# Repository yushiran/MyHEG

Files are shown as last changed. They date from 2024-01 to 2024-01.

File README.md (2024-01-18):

# 设计一下MyHEG(max30102)的detector pcb
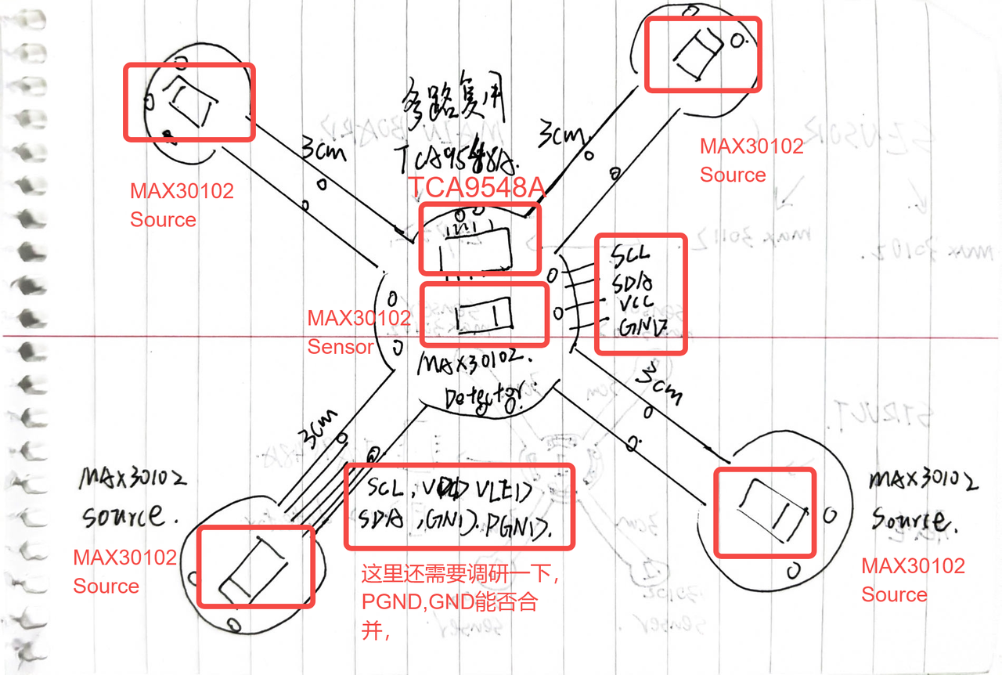
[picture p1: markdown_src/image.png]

## 设计思路：
要参考一下这篇review：https://joi.usst.edu.cn/html/2022/5/20220501.htm

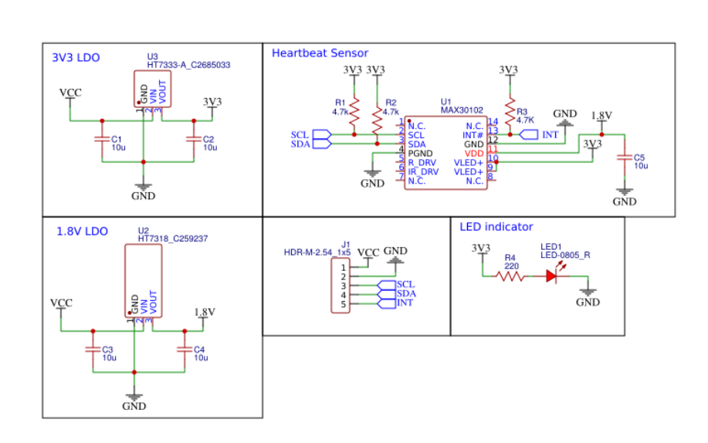
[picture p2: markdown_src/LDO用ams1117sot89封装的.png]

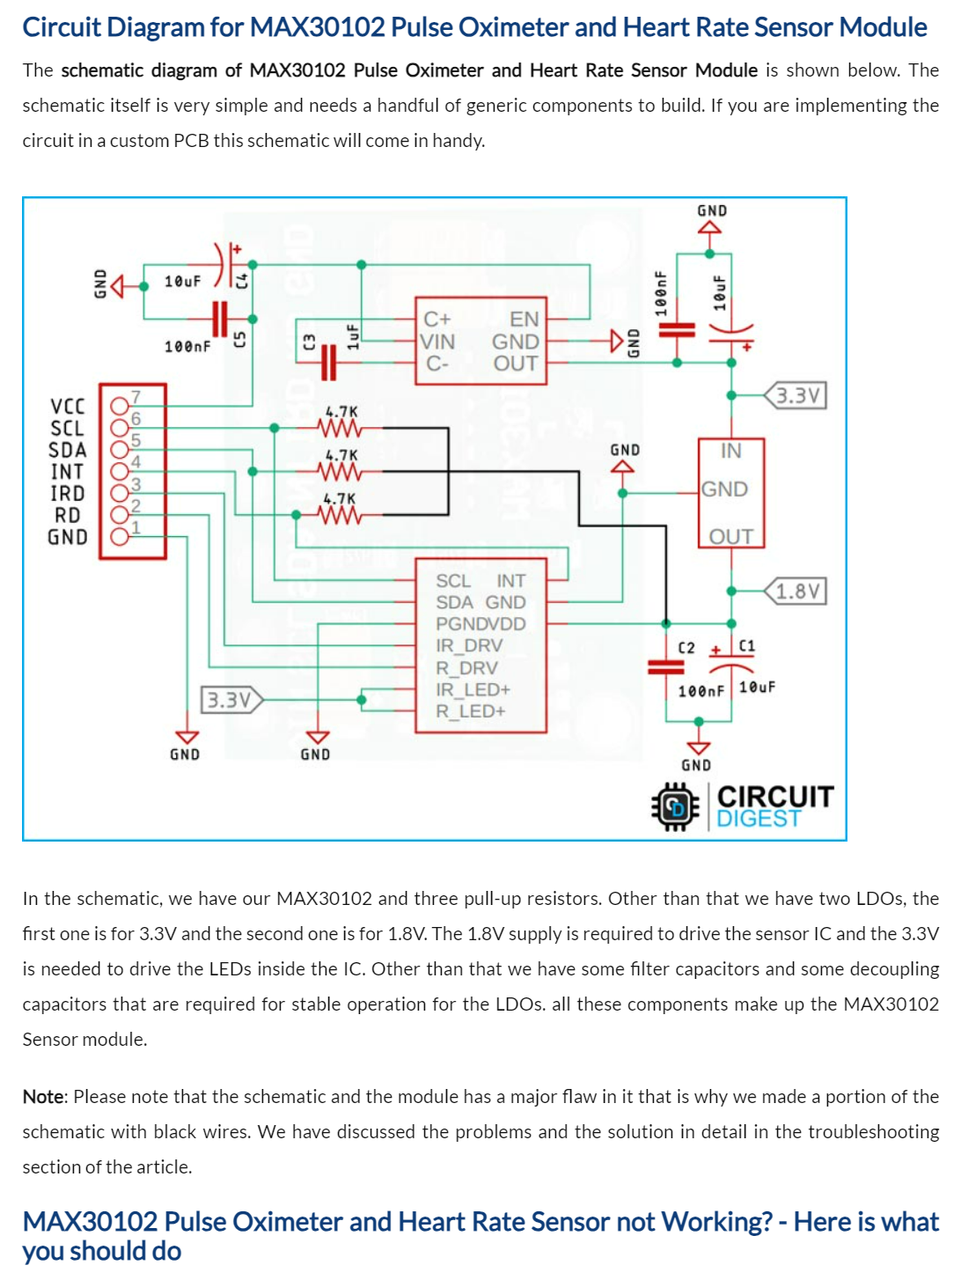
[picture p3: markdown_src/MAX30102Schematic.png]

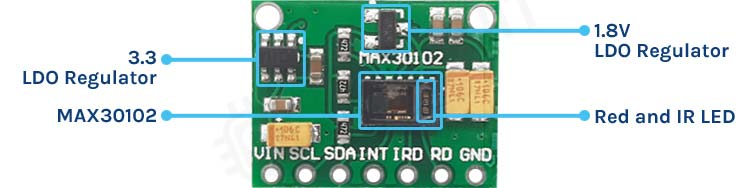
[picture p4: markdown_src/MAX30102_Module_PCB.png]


参考这个项目的思路：https://github.com/joshbrew/HEGduino_V0?tab=readme-ov-file#known-issues

利用5个MAX30102芯片来实现一个柔性PCB HEG探头的设计，5个芯片中四个为光源source，处在四个伸出的触手上，上面要打两个小洞，从而好缝，触手上的四个MAX30102作为光源在正常工作中是不需要通信，所以我们只需要在setup阶段对他们进行初始化，这里可以使用到TCA9548 I2C多路的复用器，在setup的时候咱们就选通sources们，设置他们的光源幅值，脉宽等，设置完成以后就不在和他们进行通信了，然后我们再选通处在中心的Sensor，开始检测。

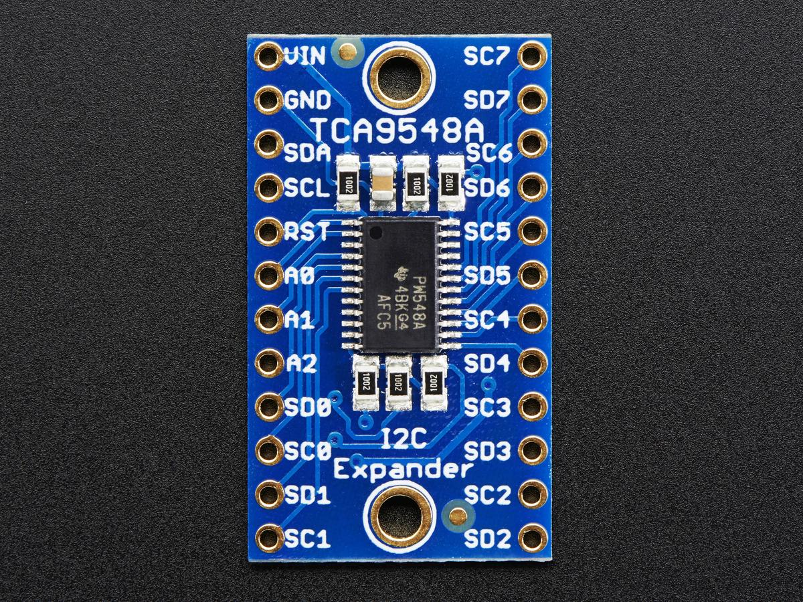
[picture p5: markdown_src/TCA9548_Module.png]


TCA9548编程指南：https://randomnerdtutorials.com/tca9548a-i2c-multiplexer-esp32-esp8266-arduino/
- 参考编程指南，依靠购买的模块简单做一个实现：
https://github.com/yushiran/MyHEG
最终期望达成的设计目标：
1. 集成度高的一个HEG模拟前端，搭配自己写的库，用尽量少的接口（一组I2C接口+VCC,GND，用一个4pin的fpc排线和main board链接）完成Sources+Sensor多个光源和一个传感器的HEG应用场景
2. 可复用性强，预留好很多用来缝线的口，可以缝制在脑电帽中，一个PCB负责一个区域的血氧监控
3. Source+Sensor均可调节，每个Source单独具有一个I2C通道，在setup阶段可以实现自定义赋值，脉宽
4. 成本较低：5*MAX30102(淘宝单价在5-12元，所以最便宜5个为25元，贵的话为60元)，TCA9548（2元），FPC制版（5个约200元，合一个40元），接插件+贴片电阻电容+电源管理芯片（预估为5元），所以成本控制最好的情况下一个模块价格为72元，最差的情况大概为107元。

## PCB设计情况
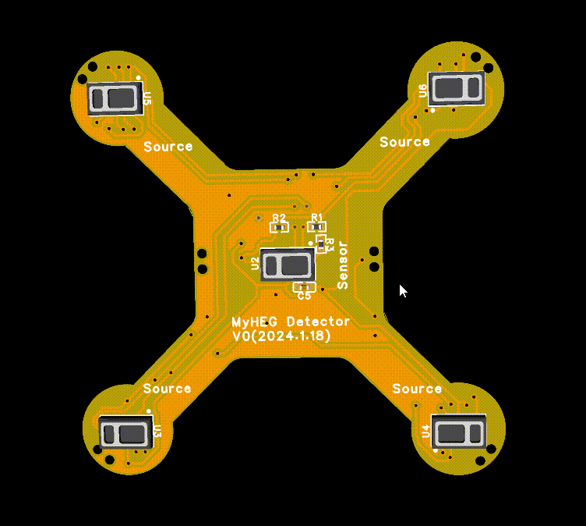
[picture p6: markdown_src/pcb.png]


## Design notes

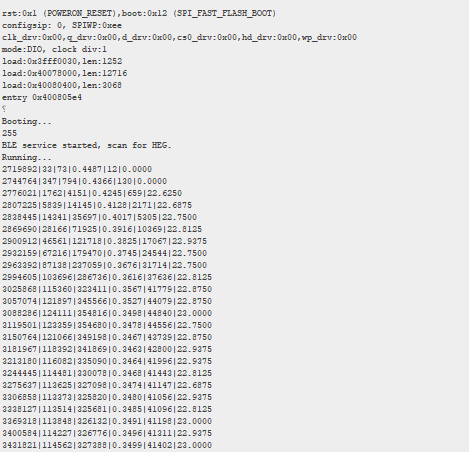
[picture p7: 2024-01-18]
MAX86141PCB/MAX86141HEG_reference/Data.PNG

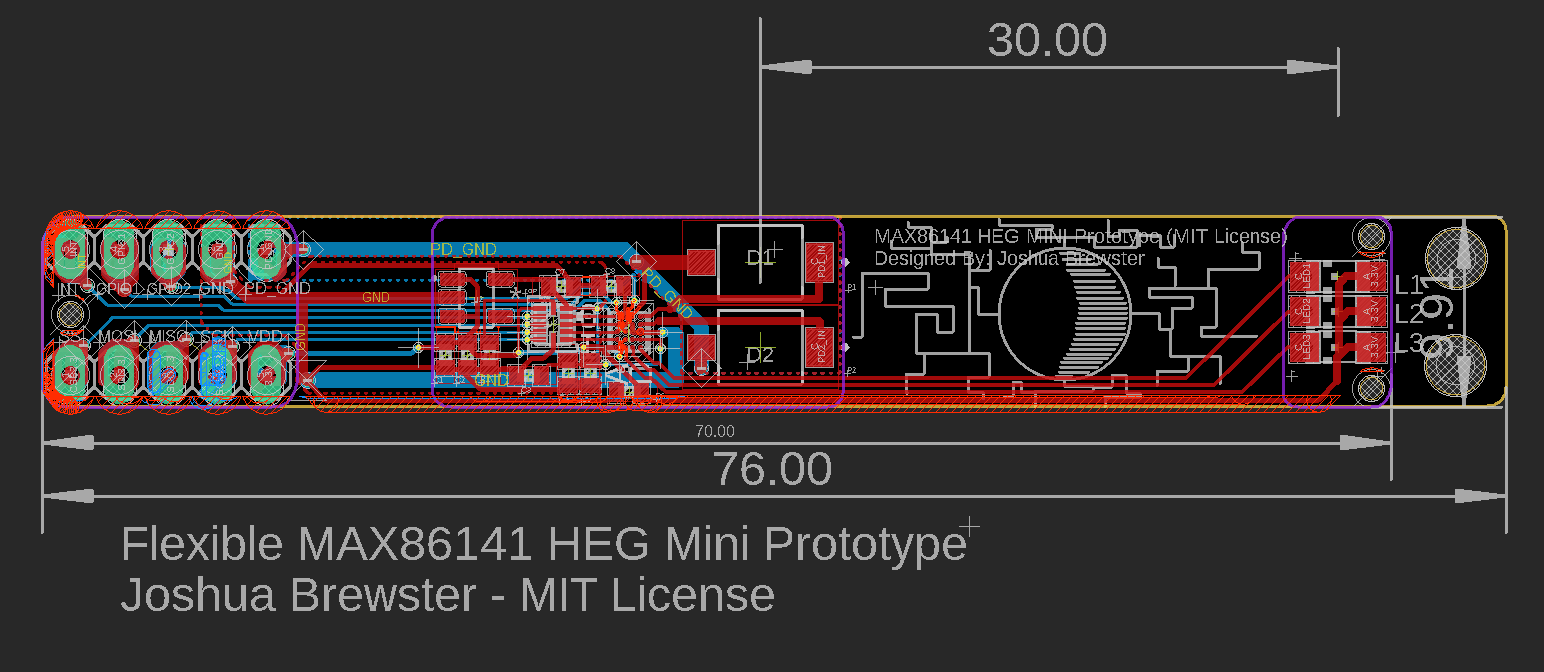
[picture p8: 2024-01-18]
MAX86141PCB/MAX86141HEG_reference/Breakout.PNG

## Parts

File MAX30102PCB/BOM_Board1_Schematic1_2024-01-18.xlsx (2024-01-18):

No. | Quantity | Comment | Designator | Footprint | Value | Manufacturer Part | Manufacturer | Supplier Part | Supplier | Pins | LCSC Stock | Primary Category | Secondary Category | LCSC Price | JLCPCB Stock | JLCPCB Price | Add into BOM | Convert to PCB | 3D Model Title | Device | Name | Unique ID | 3D Model Transform | Description | Datasheet | JLCPCB Part Class | LCSC Part Name | Origin Footprint | Supplier Footprint
1 | 10 | 10uF | C1,C2,C3,C4,C5,C6,C7,C8,C9,C10 | C0402 | 10uF | CL05A106MQ5NUNC | SAMSUNG(三星) | C15525 | LCSC | 2 | 99637 | 电容 | 贴片电容(MLCC) | 0.030332 | 10215523 | 0.0303 | yes | yes | C0402_L1.0-W0.5-H0.5 | CL05A106MQ5NUNC | 10uF | gge2,gge3,gge5,gge6,gge12,gge17,gge22,gge27,gge32,gge34 | 39.37,19.685,0,0,0,0,0,0,0 | 容值:10uF;精度:±20%;额定电压:6.3V;材质(温度系数):X5R; | https://atta.szlcsc.com/upload/public/pdf/source/20220823/2B02EE04F8F211D38A52DCB16EB6BEBA.pdf |  | 10uF ±20% 6.3V |  | 0402
2 | 1 | HC-FPC-05-09-4RLTAG | FPC1 | FPC-SMD_4P-P0.50_HC-FPC-05-09-4RLTAG |  | HC-FPC-05-09-4RLTAG | HCTL(华灿天禄) | C5213746 | LCSC | 6 | 4391 | 连接器 | FFC/FPC连接器 | 0.500905 | 19513 | 0.501 | yes | yes | FPC-SMD_4P-P0.50_HC-FPC-05-09-4RLTAG | HC-FPC-05-09-4RLTAG | HC-FPC-05-09-4RLTAG | gge7 | 157.8737,137.795,0,0,0,0,0,-1.378,0 | 锁定特性:翻盖式;触点类型:双侧触点/上下接;触点数量:4P;间距:0.5mm;安装类型:卧贴;工作温度范围:-;焊接温度(最大值):-; | https://atta.szlcsc.com/upload/public/pdf/source/20221026/52A26161A88FCE07A06989F8D4399614.pdf |  | 翻盖式 双侧触点/上下接 P数:4P 间距:0.5mm |  | SMD,P=0.5mm,卧贴
3 | 1 | AMS1117-3.3V | Q1 | SOT-89-3_L4.5-W2.5-P1.50-LS4.2-BR |  | AMS1117-3.3V | MSKSEMI(美森科) | C5120796 | LCSC | 3 | 15548 | 电源芯片 | 线性稳压器(LDO) | 0.268046 | 89499 | 0.268 | yes | yes | SOT-89-3_L4.3-W2.5-H1.6-LS4.1-P1.50 | AMS1117-3.3V_C5120796 | AMS1117-3.3V | gge1 | 161.417,169.291,0,180,0,0,-11.808,0,0 | 输出类型:固定;最大输入电压:18V;输出电压:3.3V;最大输出电流:1A;输出极性:正极; | https://atta.szlcsc.com/upload/public/pdf/source/20231123/6117526697EB8BF6175FDEEBA0877266.pdf |  | 输入18V 输出3.3V 1A |  | SOT-89
4 | 18 | 4.7kΩ | R1,R2,R3,R4,R5,R6,R7,R8,R9,R10,R11,R12,R13,R14,R15,R16,R17,R18 | R0402 | 4.7kΩ | 0402WGF4701TCE | UNI-ROYAL(厚声) | C25900 | LCSC | 2 | 56088 | 电阻 | 贴片电阻 | 0.003063 | 4572435 | 0.00306 | yes | yes | R0402_L1.0-W0.5-H0.5 | 0402WGF4701TCE | 4.7kΩ | gge9,gge10,gge11,gge14,gge15,gge16,gge19,gge20,gge21,gge24,gge25,gge26,gge29,gge30,gge31,gge35,gge36,gge37 | 39.37,19.685,0,0,0,0,0,0.0005,0 | 阻值:4.7kΩ;精度:±1%;功率:62.5mW;温度系数:±100ppm/℃;电阻类型:厚膜电阻; | https://atta.szlcsc.com/upload/public/pdf/source/20200306/C422600_1E6D84923E4A46A82E41ADD87F860B5C.pdf |  | 4.7kΩ ±1% 62.5mW 厚膜电阻 |  | 0402
5 | 1 | AMS1117-1.8 | U1 | SOT-89-3_L4.5-W2.5-P1.50-LS4.2-BR |  | AMS1117-1.8 | Slkor(萨科微) | C880751 | LCSC | 3 | 523 | 电源芯片 | 线性稳压器(LDO) | 0.482416 | 990 | 0.482 | yes | yes | SOT-89-3_L4.3-W2.5-H1.6-LS4.1-P1.50 | AMS1117-1.8_C880751 | AMS1117-1.8 | gge4 | 161.417,169.291,0,180,0,0,-11.808,0,0 | 输出类型:-; | https://atta.szlcsc.com/upload/public/pdf/source/20190906/C426566_95BE246DE70C248781207323626ADB09.pdf |  | AMS1117-1.8 |  | SOT-89-3
6 | 5 | MAX30102EFD+T | U2,U3,U4,U5,U6 | OESIP-14_L5.6-W3.3-P0.80-TL |  | MAX30102EFD+T | ADI(亚德诺)/MAXIM(美信) | C6454833 | LCSC | 14 | 506 | 传感器 | 心率传感器 | 39.84 | 461 | 39.84 | yes | yes | OESIP-14_L5.6-W3.3-P0.80-TL | MAX30102EFD+T_1 | MAX30102EFD+T | gge8,gge13,gge18,gge23,gge28 | 129.921,220.472,0,0,0,0,0,0.004,0 |  | https://atta.szlcsc.com/upload/public/pdf/source/20230523/5357A0E2EBB238F1082B332F3131EA1A.pdf |  | MAX30102EFD+T |  | OESIP-14
7 | 1 | TCA9548APWR | U7 | TSSOP-24_L7.8-W4.4-P0.65-LS6.4-BL |  | TCA9548APWR | TI(德州仪器) | C130026 | LCSC | 24 | 14513 | 逻辑器件 | 信号开关/编解码器/多路复用器 | 3.02 | 15007 | 3.02 | yes | yes | TSSOP-24_L7.8-W4.4-H1.0-LS6.4-P0.65 | TCA9548APWR | TCA9548APWR | gge33 | 252.188,307.086,0,90,0,0,0,0,0 | 类型:总线开关;电压-电源:1.65V ~ 5.5V;电路:1 x 8：1;电压源:单电源;逻辑电路的归属系列:TCA; | https://atta.szlcsc.com/upload/public/pdf/source/20170918/C130026_1505703263473975110.pdf |  | TCA9548APWR |  | TSSOP-24

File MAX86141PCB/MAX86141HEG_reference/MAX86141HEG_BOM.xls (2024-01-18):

Id | Designator | Package | Qty/unit | Designation | More Info | Digikey Cost | 1 | 10 | 100 | 1000
1 | U1 | 20 Bumps Thin WLP | 1 | MAX86141ENP+T | https://pdfserv.maximintegrated.com/package_dwgs/21-100134.PDF |  | 7.38 | 66.65 | 551.8 | 4185
2 | D1,D2 |  | 2 | BPW 34 S-Z | https://www.mouser.com/ProductDetail/OSRAM-Opto-Semiconductors/BPW-34-S-Z?qs=K5ta8V%252BWhtbaD%252B%252BL55sGPw%3D%3D |  | 1.02 | 6.65 | 43.57 | 435.7
3 | L1 | 1206 | 1 | XZTHI55W-3 | LED Indication - Discrete 1.2V 1206 (3016 Metric) 880nm
4 | L2 | 1206 | 1 | XZTNI55W-3 | LED Indication - Discrete 1.2V 1206 (3016 Metric) 940nm |  | 0.5 | 3.61 | 23.56 | 132.5
5 | L3 | 1206 | 1 | XZM2MR55W-3 | LED RED CLEAR 3216 SMD 660nm |  | 0.48 | 3.41 | 19.88 | 113.62
6 | C4,C6 | C0402 | 2 | GRM155R60G106ME44D | Multilayer Ceramic Capacitors MLCC - SMD/SMT 0402 10uF 4.0volts X5R 20% |  | 0.2 | 1.36 | 6.9 | 41.77
7 | C1,C2,C3,C7,C8 | C0402 | 5 | EMK105BJ105MVHF | Multilayer Ceramic Capacitors MLCC - SMD/SMT 0402 16VDC 1uF 20% X5R AEC-Q200 |  | 0.1 | 0.46 | 2.05 | 11.5
8 | C5 | C0402 | 1 | EMF105B7104MVHF | Multilayer Ceramic Capacitors MLCC - SMD/SMT 0402 16V 0.1uF 20% AEC-Q200 CER 0.1UF 6.3V X5R 0603 |  | 0.18 | 1.26 | 5.94 | 34.5
9 | R1 | R0402 | 1 | RG1005P-103-D-T10 | Thin Film Resistors - SMD 1/16W 10K Ohms 0.5% 0402 25ppm |  | 0.14 | 1.27 | 4.9 | 21.56
10 | U2 | SOT-23-5 | 1 | LP5907MFX-1.8/NOPB | LDO Voltage Regulators 250mA Ultra-Lo Noise LDO Reg |  | 0.55 | 4.31 | 32 | 191
11 | U3 |  | 1 | TXBN0304RUTR | 3.3v to 1.8V bidirectional 4-channel voltage regulator
 |  |  | 17 |  |  | TOTALS | 10.55 | 88.98 | 690.6 | 5167.15

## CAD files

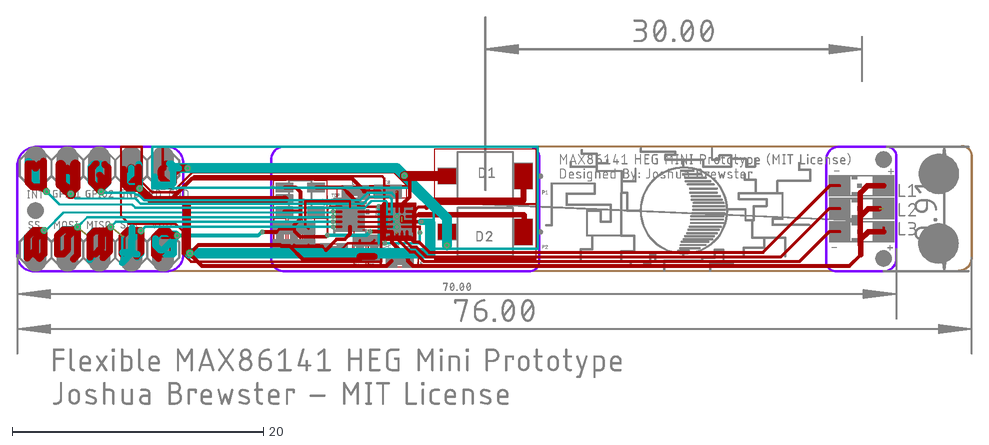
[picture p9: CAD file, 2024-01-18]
MAX86141PCB/MAX86141HEG_reference/MAX86141_HEG_MINI.dxf
76.2 x 30.9

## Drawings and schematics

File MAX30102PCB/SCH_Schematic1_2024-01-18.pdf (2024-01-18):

# 3V3 LDOVIN

# 1V8 LDOVIN

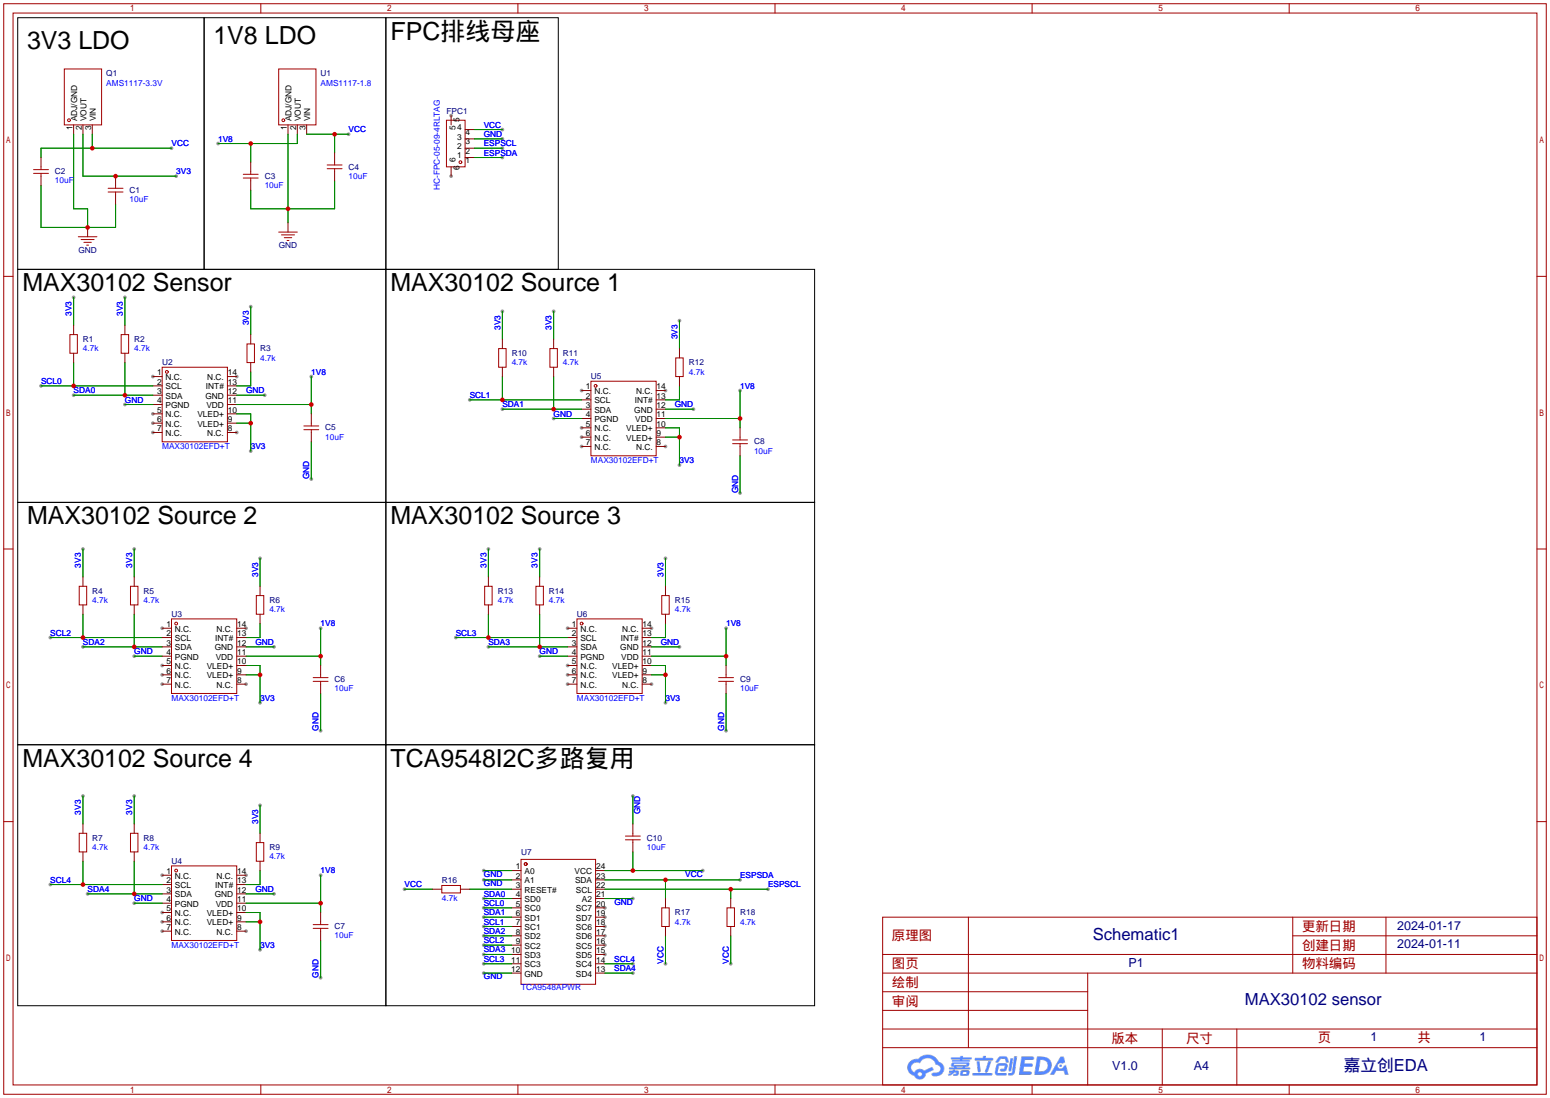
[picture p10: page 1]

VLED+ 10 VDD 11 GND 12 INT# 13 N.C. 14

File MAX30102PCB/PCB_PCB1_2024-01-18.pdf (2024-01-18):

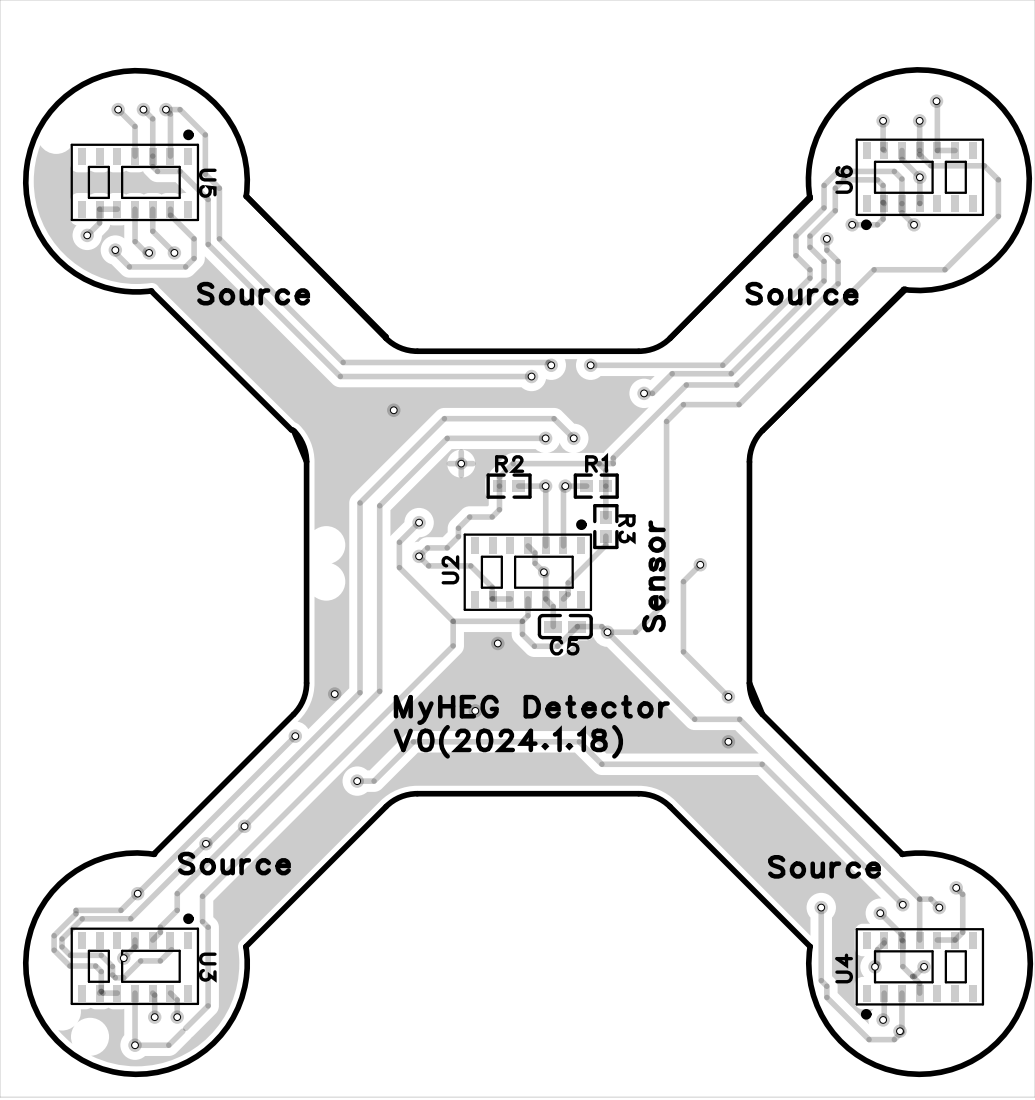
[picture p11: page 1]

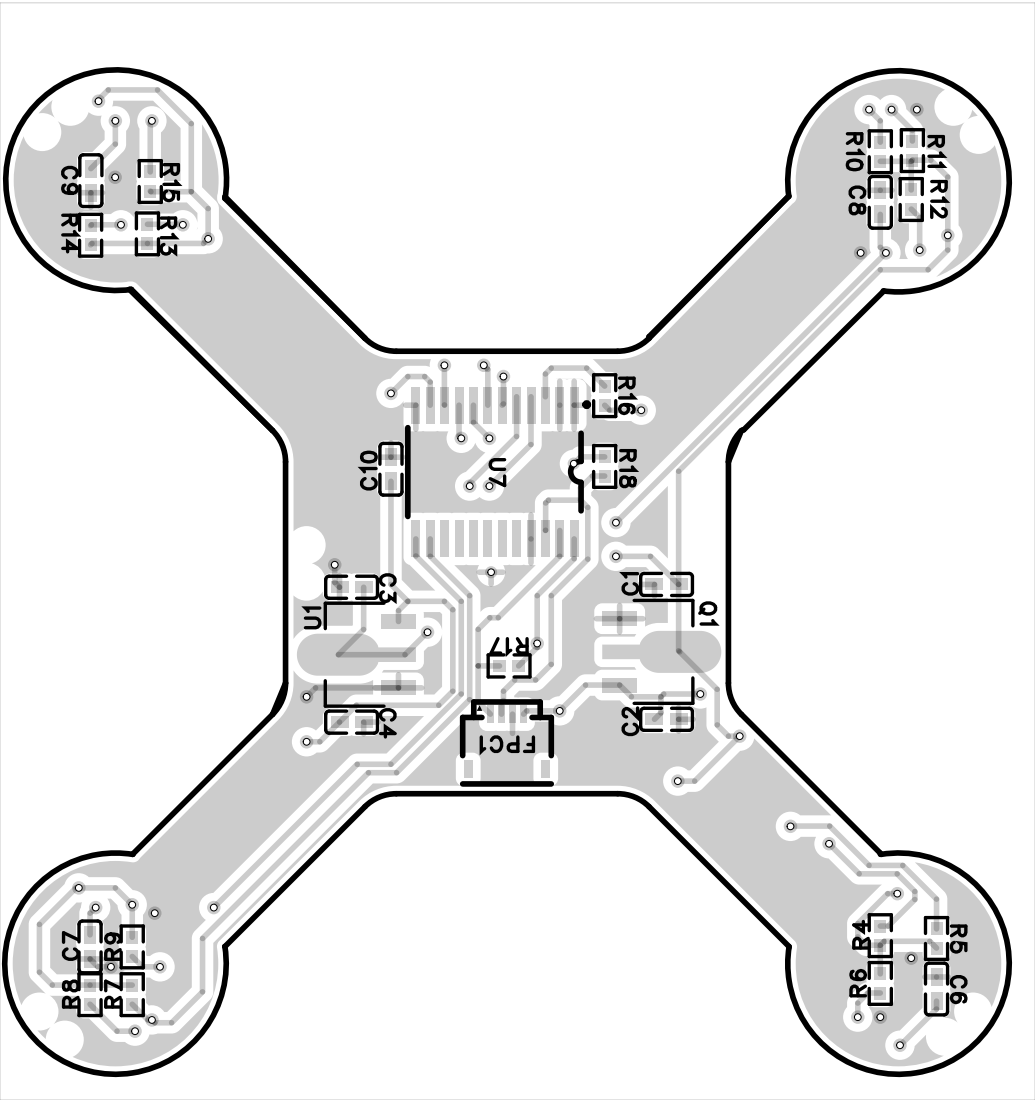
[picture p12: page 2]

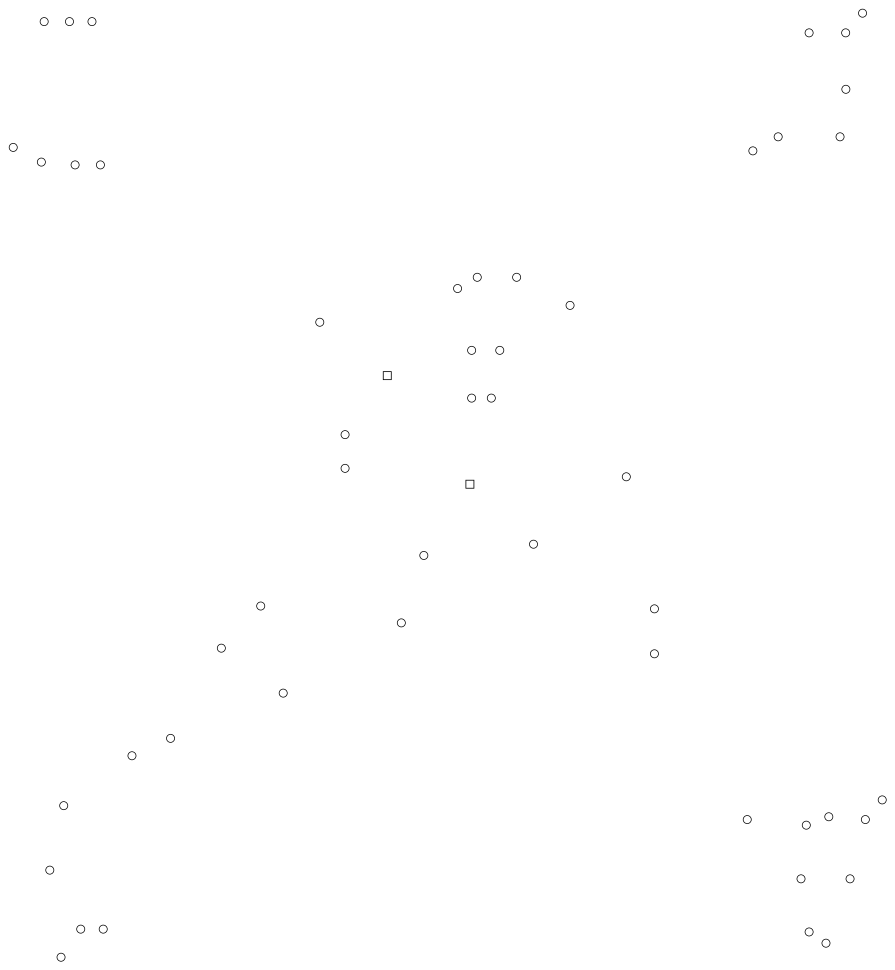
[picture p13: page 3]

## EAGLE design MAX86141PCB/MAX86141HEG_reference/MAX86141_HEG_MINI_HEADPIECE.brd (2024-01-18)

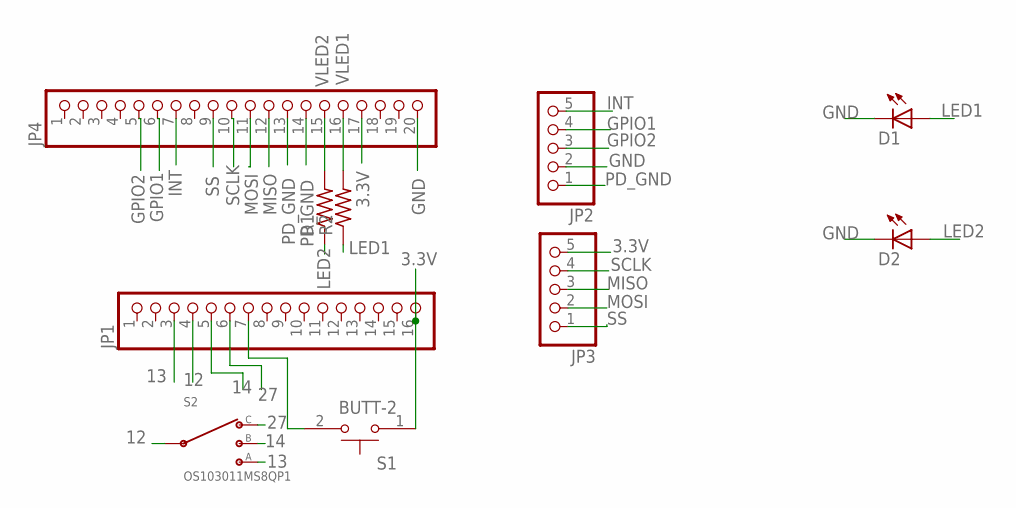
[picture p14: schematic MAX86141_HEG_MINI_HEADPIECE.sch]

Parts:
D1, D2: LED1206; LED-1206
JP1: PINHD-1X16; 1X16
JP2, JP3: PINHD-1X5; 1X05
JP4: PINHD-1X20; 1X20
R1, R2: R-US_0204/5; 0204/5
S1: BUTT-2; SW_BUTT-2
S2: OS103011MS8QP1; OS102011MS8QP1

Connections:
3.3V: JP1.16, JP3.5, JP4.17, S1.1
12: JP1.4, S2.2 (C)
13: JP1.3, S2.1
14: JP1.5, S2.3 (2)
27: JP1.6, S2.4 (3)
GND: D1.C, D2.C, JP2.2, JP4.20
GPIO1: JP2.4, JP4.6
GPIO2: JP2.3, JP4.5
INT: JP2.5, JP4.7
LED1: D1.A, R2.1
LED2: D2.A, R1.1
MISO: JP3.3, JP4.12
MOSI: JP3.2, JP4.11
unnamed: JP1.7, S1.2
PD_GND: JP2.1, JP4.13, JP4.14
SCLK: JP3.4, JP4.10
SS: JP3.1, JP4.9
VLED1: JP4.16, R2.2
VLED2: JP4.15, R1.2

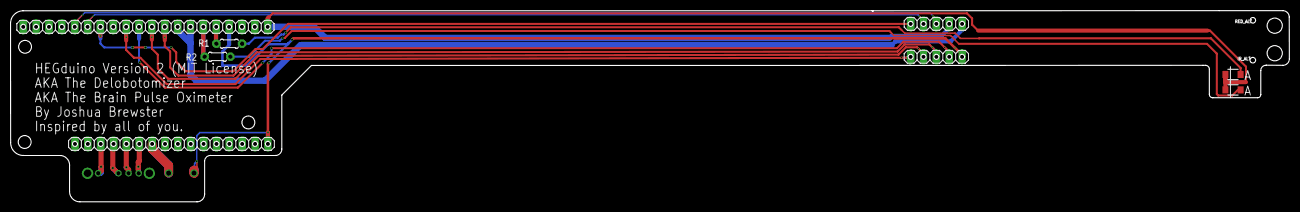
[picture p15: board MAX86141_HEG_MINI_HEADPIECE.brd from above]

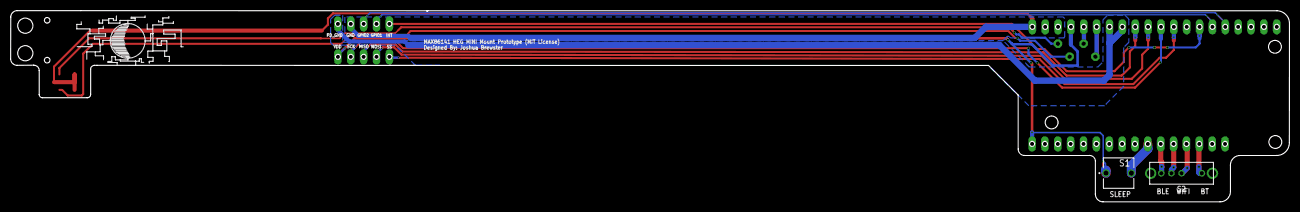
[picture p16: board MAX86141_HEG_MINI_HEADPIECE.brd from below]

Board: 2 copper layers, 252.5 x 37.7 mm, 10 parts (2 on the bottom side), 19 nets.

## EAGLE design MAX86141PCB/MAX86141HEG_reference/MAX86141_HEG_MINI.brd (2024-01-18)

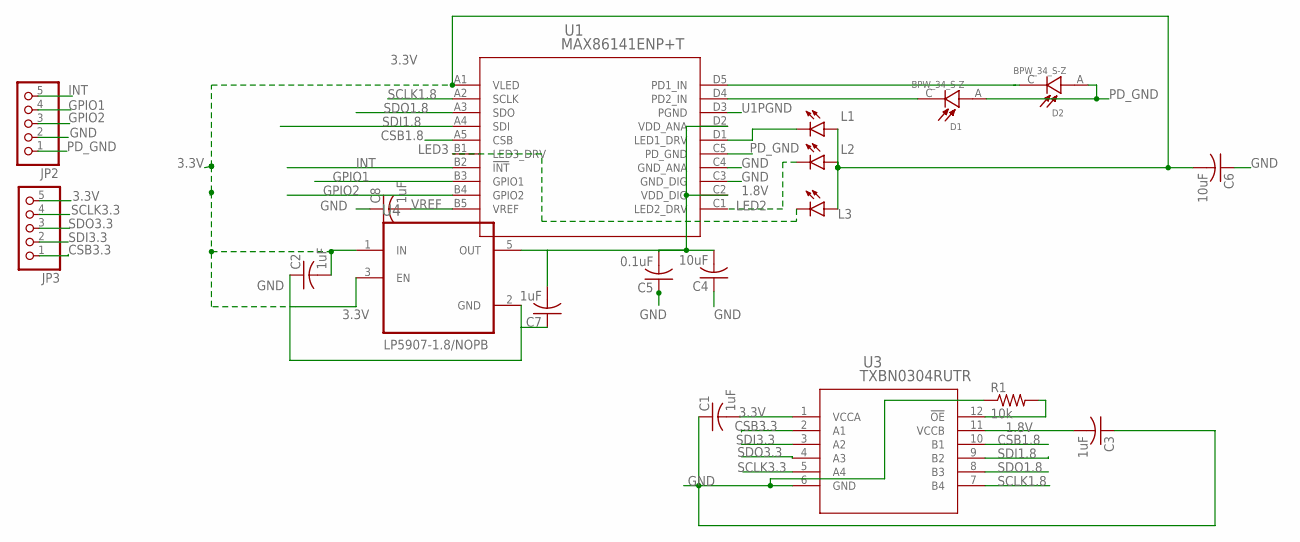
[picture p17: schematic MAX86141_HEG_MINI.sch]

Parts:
C1, C2, C3, C7, C8: 1uF; C0402
C4, C6: 10uF; C0402
C5: 0.1uF; C0402
D1, D2: BPW_34_S-Z; DIO_BPW_34_S-Z
JP2, JP3: PINHD-1X5; 1X05
L1, L2, L3: LEDCHIPLED_1206; CHIPLED_1206
R1: 10k; R0402
U1: MAX86141ENP+T; 21-100134A_20
U3: TXBN0304RUTR; RUT12
U4: LP5907MFX-3.3/NOPB; SOT95P280X145-5N

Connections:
1.8V: C3.2, C4.2, C5.2, C7.2, U1.C2 (VDD_DIG), U1.D2 (VDD_ANA), U3.11 (VCCB), U4.5 (OUT)
3.3V: C1.2, C2.2, C6.2, JP3.5, L1.A, L2.A, L3.A, U1.A1 (VLED), U3.1 (VCCA), U4.1 (IN), U4.3 (EN)
CSB1.8: U1.A5 (CSB), U3.10 (B1)
CSB3.3: JP3.1, U3.2 (A1)
GND: C1.1, C2.1, C3.1, C4.1, C5.1, C6.1, C7.1, C8.1, JP2.2, R1.1, U1.C3 (GND_DIG), U1.C4 (GND_ANA), U3.6 (GND), U4.2 (GND)
GPIO1: JP2.4, U1.B3 (GPIO1)
GPIO2: JP2.3, U1.B4 (GPIO2)
INT: JP2.5, U1.B2 (!INT)
LED1: L1.C, U1.D1 (LED1_DRV)
LED2: L2.C, U1.C1 (LED2_DRV)
LED3: L3.C, U1.B1 (LED3_DRV)
OE: R1.2, U3.12 (!OE)
PD1_IN: D2.C, U1.D5 (PD1_IN)
PD2_IN: D1.C, U1.D4 (PD2_IN)
PD_GND: D1.A, D2.A, JP2.1, U1.C5 (PD_GND)
SCLK1.8: U1.A2 (SCLK), U3.7 (B4)
SCLK3.3: JP3.4, U3.5 (A4)
SDI1.8: U1.A4 (SDI), U3.9 (B2)
SDI3.3: JP3.2, U3.3 (A2)
SDO1.8: U1.A3 (SDO), U3.8 (B3)
SDO3.3: JP3.3, U3.4 (A3)
U1PGND: U1.D3 (PGND)
VREF: C8.2, U1.B5 (VREF)

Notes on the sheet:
LP5907-1.8/NOPB

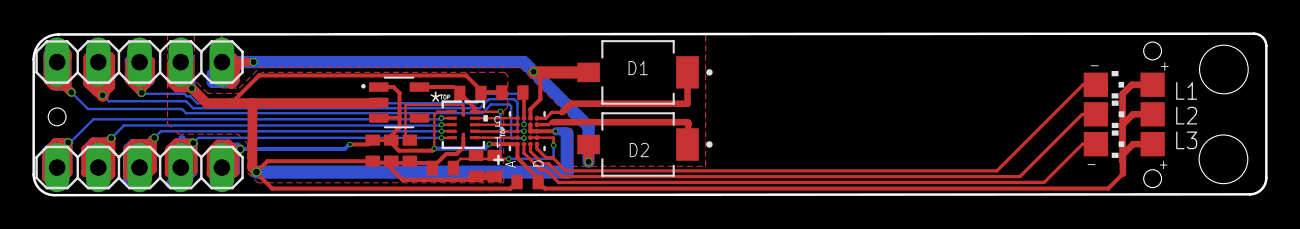
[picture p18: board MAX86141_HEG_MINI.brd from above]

Board: 2 copper layers, 76.0 x 10.0 mm, 19 parts (0 on the bottom side), 22 nets.

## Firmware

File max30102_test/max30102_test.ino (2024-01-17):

#include <Wire.h>
#include "src/MAX30105.h"

MAX30105 Sensor1;
MAX30105 Sensor2;
#define SDA_1 21
#define SCL_1 22
#define SDA_2 4
#define SCL_2 5
TwoWire I2C_1 = TwoWire(0);
TwoWire I2C_2 = TwoWire(1);
#define debug Serial

void setup()
{
  delay(2000);
  debug.begin(115200);
  debug.println("MAX30105 Basic Readings Example");
  // Initialize sensor
  I2C_1.begin(SDA_1, SCL_1);
  I2C_2.begin(SDA_2, SCL_2); 
  Sensor1.begin(I2C_1);
  Sensor2.begin(I2C_2);


  uint8_t LEDpwr = 255;
  uint8_t sAvg = 8;
  uint16_t sRate = 3200;
  uint8_t ledMode = 2;
  uint8_t pulseWidth = 69;
  uint16_t adcRange = 16384;

  // Sensor1.setup(LEDpwr, 1, ledMode, 800, 118, adcRange);
  // Sensor2.setup(0x00, sAvg, ledMode, sRate, pulseWidth, adcRange);

  Sensor1.setup(); //Configure sensor. Use 6.4mA for LED drive
  Sensor2.setup();
}

void loop()
{
  // Serial.print(Sensor1.getRed());
  // Serial.print(", ");
  // Serial.print(Sensor1.getIR());
  // Serial.print(", ");
  Serial.print(Sensor2.getRed());
  Serial.print(", ");
  Serial.print(Sensor2.getIR());
  Serial.println();

}

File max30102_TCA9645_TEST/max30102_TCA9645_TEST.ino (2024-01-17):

#include <Wire.h>
#include "src/MAX30105.h"
#include <Adafruit_Sensor.h>

MAX30105 Sensor1;
MAX30105 Sensor2;
#define SDA_1 21
#define SCL_1 22
#define SDA_2 4
#define SCL_2 5
TwoWire I2C_1 = TwoWire(0);
TwoWire I2C_2 = TwoWire(1);
#define debug Serial

// Select I2C BUS
void TCA9548A(uint8_t bus){
  Wire.beginTransmission(0x70);  // TCA9548A address
  Wire.write(1 << bus);          // send byte to select bus
  Wire.endTransmission();
}

void printValues(MAX30105 Sensor, int bus) {
  TCA9548A (bus);
  Serial.print(Sensor.getRed());
  Serial.print(", ");
  Serial.print(Sensor.getIR());
  Serial.println();
}

void setup()
{
  delay(2000);
  debug.begin(115200);
  debug.println("MAX30105 Basic Readings Example");
  // Initialize sensor
  I2C_1.begin(SDA_1, SCL_1);
  I2C_2.begin(SDA_2, SCL_2); 
  TCA9548A(2);
  Sensor1.begin();
  Sensor1.setup(); //Configure sensor. Use 6.4mA for LED drive
  TCA9548A(3);
  Sensor2.begin();
  Sensor2.setup();


  uint8_t LEDpwr = 255;
  uint8_t sAvg = 8;
  uint16_t sRate = 3200;
  uint8_t ledMode = 2;
  uint8_t pulseWidth = 69;
  uint16_t adcRange = 16384;

  // Sensor1.setup(LEDpwr, 1, ledMode, 800, 118, adcRange);
  // Sensor2.setup(0x00, sAvg, ledMode, sRate, pulseWidth, adcRange);
}

void loop()
{
  printValues(Sensor1, 2);
  printValues(Sensor2, 3);
}

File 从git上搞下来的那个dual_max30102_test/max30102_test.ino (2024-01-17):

#include "src/MAX30105.h"
#include <Wire.h>

MAX30105 PPG1;
MAX30105 PPG2;

#define SDA 21
#define SCL 22

#define SDA1 4
#define SCL1 5

long long currentMillis = 0;

int maxR2 = 0;
int maxIR2 = 0;
byte redct = 0;
byte irct = 0;
int smpct = 0;

byte irctmax = 32; //number of samples before the IR oscillates back to zero (due to desynchronized MAX30102 sensors with one taking ambient measurements trying to catch the LEDs from the other MAX30102)

void setup() {
  delay(2000);
  
  Wire.setPins(SDA,SCL);
  Wire1.setPins(SDA1,SCL1);

  Serial.begin(115200);
  Serial.println("Sensors starting");
  
  bool p1 = PPG1.begin(Wire,  I2C_SPEED_FAST);
  bool p2 = PPG2.begin(Wire1, I2C_SPEED_FAST);

  if(!p1) Serial.println("Pulse Ox 1 not found");
  if(!p2) Serial.println("Pulse Ox 2 not found");

  uint8_t LEDpwr = 255;
  uint8_t sAvg = 8;
  uint16_t sRate = 1600;
  uint8_t ledMode = 2;
  uint8_t pulseWidth = 69;
  uint16_t adcRange = 16384;

  PPG1.softReset();
  PPG2.softReset();

  PPG1.shutDown();
  PPG2.shutDown();

  //user the same settings except PPG1 flashes the LEDs
  PPG1.setup(LEDpwr, 1, ledMode, 800, 118, adcRange);

  //delayMicros(100) ///??? How to sync devices
  PPG2.setup(0x00, sAvg, ledMode, sRate, pulseWidth, adcRange);

  PPG1.wakeUp();
  PPG2.wakeUp();
}

int R2_0 = 0;
int R2_1 = 0;
int R2_2 = 0;
int R2_3 = 0;
int R2_4 = 0;


int IR2_0 = 0;
int IR2_1 = 0;
int IR2_2 = 0;
int IR2_3 = 0;
int IR2_4 = 0;

//bool cycled = false;

void readPulseOx() {
  PPG1.check();
  PPG2.check();

  while(PPG2.available()) {

  //  int R1 = PPG1.getFIFORed();
   int R2 = PPG2.getFIFORed();
  //  int IR1 = PPG1.getFIFOIR();
   int IR2 = PPG2.getFIFOIR();


    R2_4 = R2_3;
    R2_3 = R2_2;
    R2_2 = R2_1;
    R2_1 = R2_0;
    R2_0 = R2;

    IR2_4 = IR2_3;
    IR2_3 = IR2_2;
    IR2_2 = IR2_1;
    IR2_1 = IR2_0;
    IR2_0 = IR2;
      
    if(R2_2 > IR2_2) {
      if(maxR2 < R2_2 && R2_2 > R2_0 && R2_2 > R2_1 && R2_2 > R2_3 && R2_2 > R2_4) maxR2 = R2_2;
    }
    if(IR2_2 > R2_2) {
      if(maxIR2 < IR2_2 && IR2_2 > IR2_0 && IR2_2 > IR2_1 && IR2_2 > IR2_3 && IR2_2 > IR2_4) maxIR2 = IR2_2;
    }

    // if( R2_4 > 0 && IR2_4 > 0 && (IR2 > R2 && IR2_4 < R2_4) && maxR2 > 0 && maxIR2 > 0) { //switching
    //   //the lower of the two is the Red LED pulse
    //   if(maxR2 > maxIR2) {
    //     int temp = maxR2;
    //     maxR2 = maxIR2;
    //     maxIR2 = temp;  
    //   }
      
      char outputArr[200];
      sprintf(outputArr,"%d,%d",
        R2, IR2
      );
      Serial.println(outputArr);
        
      R2_4 = 0;
      R2_3 = 0;
      R2_2 = 0;
      R2_1 = 0;
      R2_0 = 0;

      IR2_4 = 0;
      IR2_3 = 0;
      IR2_2 = 0;
      IR2_1 = 0;
      IR2_0 = 0;
        
      maxR2 = 0;
      maxIR2 = 0;
    // }

    PPG1.nextSample();
    PPG2.nextSample();
  }
}

void loop() {  
  delay(50);
  readPulseOx();
}

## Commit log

2024-01-17 把之前的code都提交上去
2024-01-18 增加以下max30102的myheg pcb制版文件
    [1_P1.schdoc.schdoc, BOM_Board1_Schematic1_2024-01-18.xlsx, Drill_NPTH_Through.DRL, Drill_PTH_Through.DRL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]
2024-01-18 加入简单的markdown
2024-01-18 开始记录基于max86141的heg设备开发
    [MAX86141HEG_BOM.xls, MAX86141_HEG_MINI.brd, MAX86141_HEG_MINI.dxf, MAX86141_HEG_MINI.sch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]
2024-01-19 增加max86141的测试程序

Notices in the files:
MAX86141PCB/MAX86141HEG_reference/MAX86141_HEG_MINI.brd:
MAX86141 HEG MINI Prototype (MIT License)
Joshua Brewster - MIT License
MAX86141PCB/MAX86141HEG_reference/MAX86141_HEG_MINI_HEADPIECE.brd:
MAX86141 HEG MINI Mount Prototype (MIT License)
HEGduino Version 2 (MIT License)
